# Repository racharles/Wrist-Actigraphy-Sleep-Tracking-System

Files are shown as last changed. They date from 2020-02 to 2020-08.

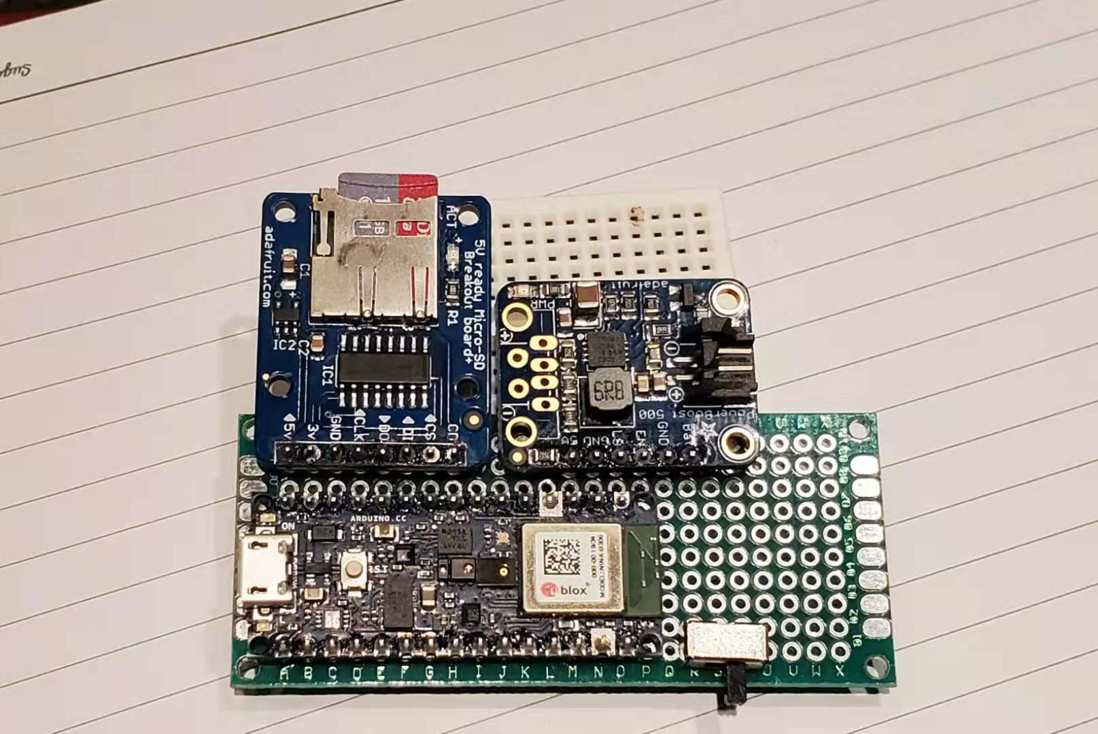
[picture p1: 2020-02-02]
Release/Hardware/WASTS V1.0 Electrical/Top View.jpg

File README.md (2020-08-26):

# Wrist Actigraphy Sleep Tracking System
Repo for the WASTS project, which entered into the 2020 LA science fair.
## Recognition
Engineering Applications Sr Division - Honorable Mention\
Darrell Smedley Award Sr Division
## References
### Academic Sources
[Stages of Sleep](https://www.sleep.org/articles/what-happens-during-sleep/)

[Interpreting PSG Reports](https://www.aastweb.org/hubfs/International%20Congress%20Presentations/4%20Atkinson%20Polysomnography%20Reports.pdf)

[Accuraccy of Wrist Actigraphy + Heart rate sensor compared to PSG](https://www.aastweb.org/hubfs/International%20Congress%20Presentations/4%20Atkinson%20Polysomnography%20Reports.pdf)

[Blood Pressure vs Sleep Quality](https://academic.oup.com/sleep/article-pdf/27/6/1097/13662447/sleep-27-6-1097.pdf)

[Comparison of Actigraphy and PSG in Older Women](https://www.ncbi.nlm.nih.gov/pmc/articles/PMC2225568/)

[Philips Actigraphy reference guide](http://www.actigraphy.com/assets/Actigraphy-reference-guide-b6bc768325426704b558b9c7288bcc07c7f636f78bec85dbafdc0814b2c62ec1.pdf)
### Datasheets
[Arduino Nano 33 BLE Sense Schematic](https://content.arduino.cc/assets/NANO33BLE_V2.0_sch.pdf)

[NINA-B3 series datasheet](https://www.u-blox.com/sites/default/files/NINA-B3_DataSheet_%28UBX-17052099%29.pdf)

[nRF52840 datasheet](https://infocenter.nordicsemi.com/pdf/nRF52840_PS_v1.1.pdf)

[LSM9DS1 datasheet](https://content.arduino.cc/assets/Nano_BLE_Sense_lsm9ds1.pdf)

[HTS221 datasheet](https://content.arduino.cc/assets/Nano_BLE_Sense_HTS221.pdf)

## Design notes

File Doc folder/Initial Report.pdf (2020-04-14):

# Low Cost Sleep Tracking with Arduino

## Rachel Bai

Purpose

The purpose of this project was to create a system that tracks the quality of sleep to decide on an appropriate wake-up time and act as advance notice for various sleep disorders.

Question

Can the quality of sleep and various sleep disorders be tracked using wrist actigraphy?

Background Research

The standard model of sleep,

Hypothesis

Main Hypothesis: Tracking the quality and health of sleep, as well as determining the optimal time for awakening, can be accomplished using wrist actigraphy.

Sub-Hypothesis: Using wrist actigraphy, movement during sleep can be detected and tracked.

Block Diagram | Schematic Diagram

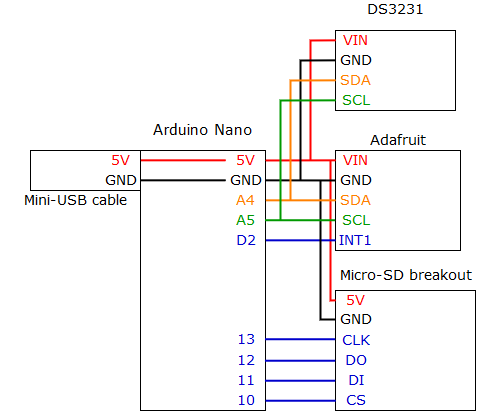
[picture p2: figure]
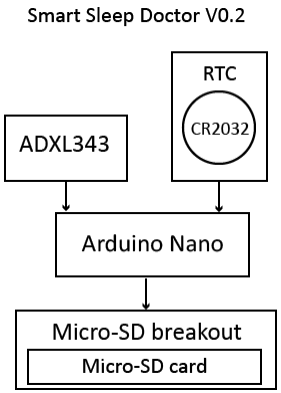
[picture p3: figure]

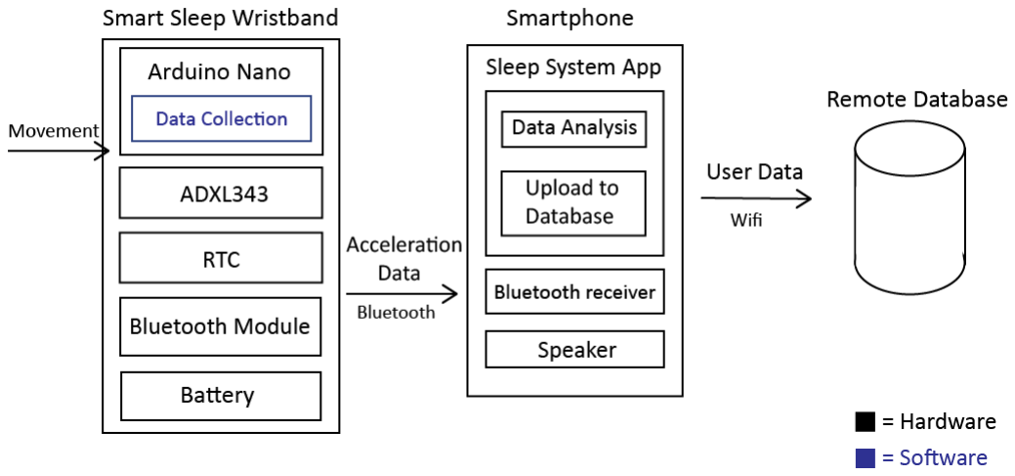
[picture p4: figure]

BOM

Name | Mass | Size | Product number | Price | Power Consumption
Arduino Nano | 7g | 18 x 45 mm | A000005 | $22 | 19 mA
Triple Axis Accelerometer breakout | 1.7g | 25.5 x 17.8 x 2.9 mm | ADXL343 | $14.95
Micro SD Storage Board | 9.1g | 25.4 x 20.32 x 2.54 mm | ADA254 | $11.89 | link (https://www.amazon.com/gp/product/B00NAY2NAI/ref=ppx_yo_dt_b_asin_title_o01_s00?ie=UTF8&psc=1)
Micro SD card | 9.1g | 1 x 15 x 10.9 mm | SDSQUAR-016G-GN6MA | $5.45 | link (https://www.amazon.com/Sandisk-Ultra-Micro-UHS-I-Adapter/dp/B073K14CVB)
Jumper Wires | 136g | 99 x 17.8 x 99 mm | B07GD2BWPY | $5.79 | link (https://www.amazon.com/EDGELEC-Breadboard-Optional-Assorted-Multicolored/dp/B07GD2BWPY?s=gateway)
RTC module | 4.5g | 43 x 22 x 15 mm | B01IXXACD0 | $6.50 | link (https://www.amazon.com/Diymore-DS3231-AT24C32-Precision-Arduino/dp/B01IXXACD0?s=gateway)
Coin cell battery | 6.8g | 30 mm diameter x 3.2 mm | B0002RID4G | $4.74 | link (https://www.amazon.com/Energizer-2032-BP-6-6-pack/dp/B0002RID4G?s=gateway)

Total Cost: $71.32

Accelerometer Comparison

We picked the ADXL343 for its range of sensitivity, low power consumption, and the built-in libraries and documentation that came with it. We also tested the MMA8451, but found that the ADXL343 had more useful features with a lower price tag.

Features | ADXL343 | ADXL335 | MMA8451
URL | https://www.adafruit.com/pr | https://www.adafruit.com/p | https://www.adafruit.com/pr
| oduct/4097 (https://www.adafruit.com/product/4097) | roduct/163 (https://www.adafruit.com/product/163) | oduct/2019 (https://www.adafruit.com/product/2019)
Dimensions | 25.5mm x 17.8mm x 2.9mm | 19mm x 19mm x 3.14mm | 21mm x 18mm x 2mm
Sensitivity range | 2-16g | 3g | 2-8g
Digital/Anal og | digital | analog | digital
# of pins | 9 | 7 | 8

Voltage | 2.0-3.6 V | 5V | 3V or 5V
Current | 23 μA | 350 μA | 6 μA to 165 μA
Weight | 1.7g | 1.27g | 1.3g
Size of IC | 3 mm × 5 mm × 1 mm | 4 mm × 4 mm × 1.45 mm | 3 mm by 3 mm by 1 mm
Additional soldering | headers | headers | headers
Interface | I2C or SPI | Analog | I2C
Integration Effort | Arduino with library | calibration and analog conversion | Arduino with library
Additional Software | library | | library
Tutorial/Exa mple | yes | calibration | yes
Interrupt pins | 2 | 2 | 2
Cost | $5.95 | $14.95 | $7.95

Software flowchart

Software design and implementation

### Final Implementation

We decided to use the Arduino Nano with the Arduino IDE for low-cost and fast prototyping. The Adafruit ADXL343 breakout board we used also came with a built-in activity interrupt, so that we were able to decrease the power consumption of the final build.

We connected the Arduino Nano, SD module, RTC, and ADXL343 based on the Schematic Diagram using a breadboard and jumper wires.

We collected data from the ADXL343 in the form of activity interrupts and printed them to the micro-SD card, along with a timestamp for each.

//print the acceleration data from the moment activity detected

data.print(event.acceleration.x); data.print(" ");

data.print(event.acceleration.y); data.print(" ");

data.println(event.acceleration.z);

//print the number of times activity detected

Serial.println("Activity detected!");

Serial.print("\tActivity Count: "); Serial.println(g_int_stats.activity, DEC);

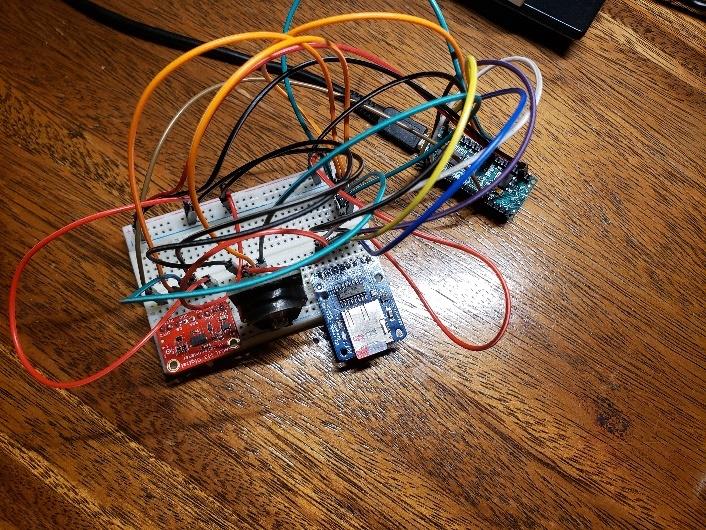
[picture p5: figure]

- Research on the standard model of sleep
- Research report placed on website
- Finished BOM and parts collected
- Acceleration on each axis printed out and stored on SD card
- RTC module added for timestamps
- Activity interrupt on ADXL343 used to notify Arduino Nano

I first did research on the standard model of sleep and collected sources about sleep and the different stages of sleep. To organize this information, I wrote a research report and put it in my website. After deciding on a schedule and two accelerometers, I added all the parts needed into the BOM and bought them online. After soldering the headers and testing the accelerometers and SD module individually, I put them together and combined the code so that the acceleration from each axis was printed in the serial monitor and micro-sd card with a timestamp. For a more efficient way to track activity, I decided to use the activity interrupt on the ADXL343 to notify the Arduino Nano. At first, the interrupt never triggered. After debugging with the example sketches and setting registers based on the datasheet, the interrupt started triggering. I adjusted the activity threshold and integrated the other components into the final sketch.

### Testing

We first tested the ADXL343 alone by outputting the data to the serial monitor and checking if it was calibrated properly.

### Evaluation

Gantt Chart

Timeline | 6/4 | 6/8 | 6/11 | 6/15 | 6/16 | 6/18 | 6/22 | 6/25 | 6/29 | 7/2
Milestones | | | Website v1.0 | | Block Diagram v1.0 | | Code for prototype | Prototype v0.1 | | Prototype v0.2
| | | Research Paper v0.5 | | Schematic v1.0 | | All parts bought
| | | | | BOM v1.0
1. Learn:
Research sleep literature

Research existing technologies

Develop project website
2. Design:
Use case

Block Diagram

BOM (parts list)

Circuit Schematic
3. Build:
Buy parts

Prototype with accelerometer

Prototype with SD and RTC
4. Test:
Test for activity sensing

Evaluate
5. Document:
website

Research report

Project Report

Results

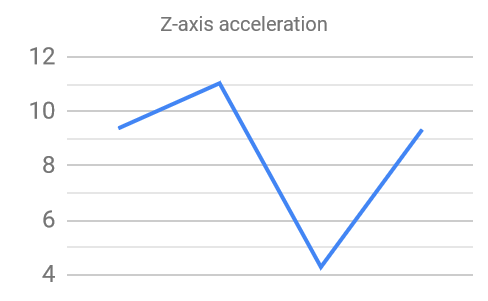
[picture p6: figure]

Upward and downward motion on z-axis

X- axis | Y-axis | Z-axis
-0.24 | 0.51 | 9.38
-1.45 | 0.2 | 11.04
-0.43 | -2.31 | 4.28 | Activity detected
-0.2 | 0.24 | 9.34

Rotation from z-axis to x-axis

X-axis | Y-axis | Z-axis
-0.24 | 0.12 | 9.38
0.9 | -0.16 | 10.63
5.96 | 0 | 6.47 Activity detected
9.07 | 0.27 | 2.71
9.85 | -0.08 | 0.9

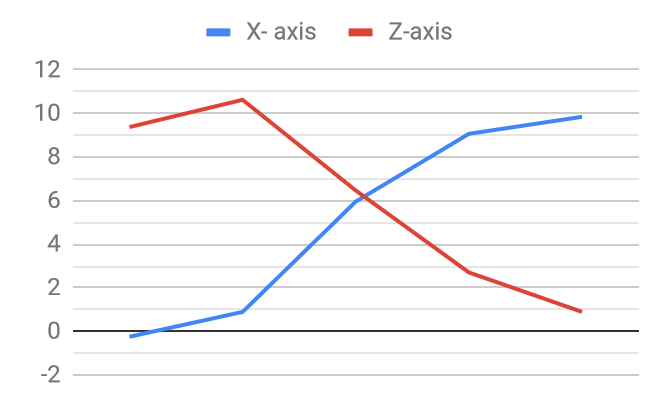
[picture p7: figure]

Lines of Code | 130
Frameworks | 1.8.9
Libraries | Wire, RTClib, SD, Adafruit_Sensor, Adafruit_ADXL343
Calibration | ADXL343 activity threshold set to 20

The activity tracking feature on the ADXL343 detects activity when the change in acceleration on any axis surpasses a certain threshold. Using a threshold is most effective in measuring larger movement, and smaller movements are often missed by the sensor. However, movements during sleep are usually small. This problem was fixed by changing the sensitivity. Because the sensor is mounted on the wrist, the two main types of movement are linear motion and rotation. The ADXL343 is able to accurately detect these types of movement. Using this system, movement during sleep can be tracked accurately.

I learned how to solder through-hole pins and the process of checking each pin to make sure the connection is reliable and there is no connection between VIN and GND, which would cause a short circuit.

We had trouble using the activity interrupt on the ADXL343, where it seemed like the Arduino was not accepting any input. When checking if the interrupt was firing by measuring the voltage of the interrupt line, there was a voltage difference, which meant the interrupt was firing, but the Arduino was not detecting it. I decided to look at the ADXL343 library and datasheet, and I saw that the library set up the single tap registers in the begin function, so we set the activity inactivity control register to 1. However, this also didn’t work. The registers had to be set in binary, so a setting of 1 did not turn everything on, it turned the last setting on. After changing the number, the activity interrupt finally started working.

In the future, we plan on integrating this part of the project into the final design by compressing the build, testing during full nights of sleep, and advancing the movement detection algorithm.

Bibliography

Full Code

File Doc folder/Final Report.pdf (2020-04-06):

# Low Cost Sleep Quality Tracking Using Arduino

## Rachel Bai

## The Webb Schools

## Abstract:

Sleep trackers that use actigraphy are a lower cost alternative to traditional overnight PSG (Polysomnography) sleep labs, and offer more mobility and access to people who might not have access to a sleep lab. However, many commercial sleep trackers can still cost more than one hundred dollars. Using Arduino in conjunction with a 3D printed case and easily accessible materials, we were able to make a cheap wrist-mounted sleep tracker that can accurately track several AASM standards of sleep, including sleep efficiency, sleep onset latency, and WASO events. After the data was collected, it was processed using Python and then R studio. A positive correlation was found between the self-reported sleeping quality measures and the device collected standards, indicating the feasibility of much lower-cost sleep trackers with Arduino. The next phase of this project would focus Bluetooth connectivity, automated data processing, and cloud-based data storage.

Introduction:

Sleep is a massively overlooked aspect of general health and cognitive function. In a poll by the National Sleep Foundation, the daily effectivity of U.S. Adults increased directly with the perceived quality of sleep[4]. For many, poor sleep quality can also be an indicator of sleeping disorders or other underlying health issues. The standard for measuring objective sleep quality is the American Academy of Sleep Medication (AASM) recommended reporting parameters, which uses total recording time (TRT), total sleep time (TST), sleep efficiency, sleep onset latency, and wake after sleep onset (WASO) events[1]. In order to measure these parameters, researchers typically use a polysomnography machine (PSG), which can often be expensive, bulky, and intrusive. The development of fitness trackers such as the Fitbit and other smart watches that use actigraphy to track sleep has introduced a lower cost option for long-term sleep quality tracking[3]. Purely actigraphy-based sleep trackers are about 60% effective in finding the different stages of sleep compared to overnight sleep studies, but are frequently more than 80% effective in determining the start and end times of periods of sleep [5].

Research Question:

Is it possible to create a wrist-mounted sleep tracker that provides a low-cost and accessible platform for long-term sleep quality tracking?

Hypothesis:

Using a low-cost data collection system built using Arduino that collects actigraphy data, several AASM sleep quality standards, including sleep efficiency, sleep onset latency, and WASO events can be tracked.

## Methodology:

Materials:

Name | Seller | Description | Price | URL
Arduino 33 BLE Sense | Arduino | small mcu with built-in sensors and BLE | $31.50 | link (https://store.arduino.cc/usa/nano-33-ble-sense-with-headers)
Micro SD Storage Board | Amazon | micro sd module for arduino | $11.89 | link (https://www.amazon.com/gp/product/B00NAY2NAI/ref=ppx_yo_dt_b_asin_title_o01_s00?ie=UTF8&psc=1)
Micro SD card | Amazon | 8 gb micro sd card | $5.45 | link (https://www.amazon.com/dp/B001CQT0X4/ref=dp_cerb_1)
Micro Lipo w/MicroUSB Jack v1 | Adafruit | micro lipo charger | $10.16 | link (https://www.amazon.com/gp/product/B00MJ0HOKS/ref=ppx_yo_dt_b_asin_title_o03_s01?ie=UTF8&psc=1)
Adafruit PowerBoost 500 | Adafruit | 3.7v to 5v booster | $11.52 | link (https://www.amazon.com/Adafruit-PowerBoost-500-Basic-ADA1903/dp/B00OKJFKEI?s=electronics)
Lithium Ion Polymer Battery - 3.7v 1000mAh | Amazon | lipo battery | $9.99 | link (https://www.amazon.com/1000mAh-battery-Rechargeable-Lithium-Connector/dp/B07BTW7CJY)
Nylon watch straps | Amazon | nylon black watch straps with buckles | $11.99 | link (https://www.amazon.com/BARTON-Watch-Bands-Choice-Standard/dp/B015NKHV2G)
Medical felt padding | Amazon | 1/8 inch felt adhesive for medical use | $18.45 | link (https://www.amazon.com/gp/product/B0053D30TC/ref=ppx_yo_dt_b_asin_title_o05_s00?ie=UTF8&psc=1)
3-pin switch | Polulu | 3 pin mini slide switch | $1.50 | link (https://www.pololu.com/product/1408)
Stranded wire kit | Amazon | 22 awg stranded core wire | $18.99 | link (https://www.amazon.com/gp/product/B00B4ZQ3L0/ref=ppx_yo_dt_b_asin_title_o00_s00?ie=UTF8&psc=1)
Tacklife Digital Multimeter | Amazon | digital multimeter | $26.97 | link (https://www.amazon.com/Tacklife-DM01M-Multimeter-Detection-Temperature/dp/B01M7ZD1VN)
Soldering Station | Amazon | Weller 40 watt soldering station | $38.97 | link (https://www.amazon.com/Weller-WLC100-40-Watt-Soldering-Station/dp/B000AS28UC)
Solder Wire | Amazon | 60/40 solder wire, 0.8mm | $7.99 | link (https://www.amazon.com/MAIYUM-63-37-Solder-Electrical-Soldering/dp/B075WB98FJ?s=hi)
3/8 inch screws | Ace Hardware | 3/8 inch pan head screws | $0.30 | link (https://www.acehardware.com/departments/hardware/screws-and-anchors/sheet-metal-screws/56192)

Hardware:

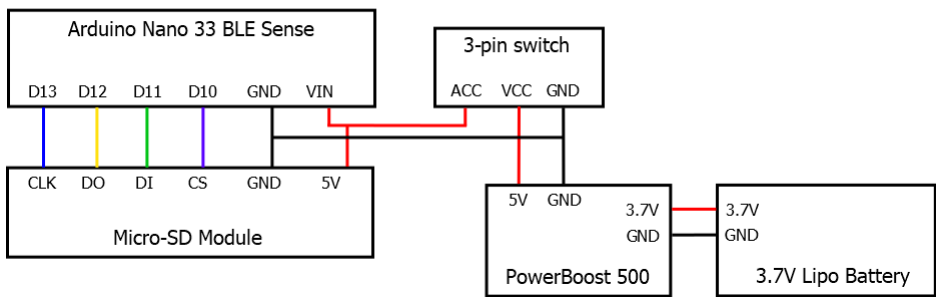
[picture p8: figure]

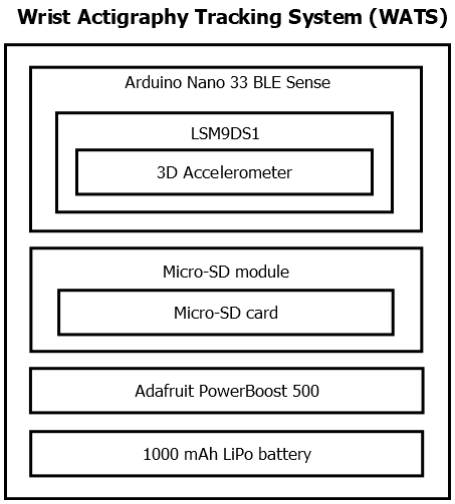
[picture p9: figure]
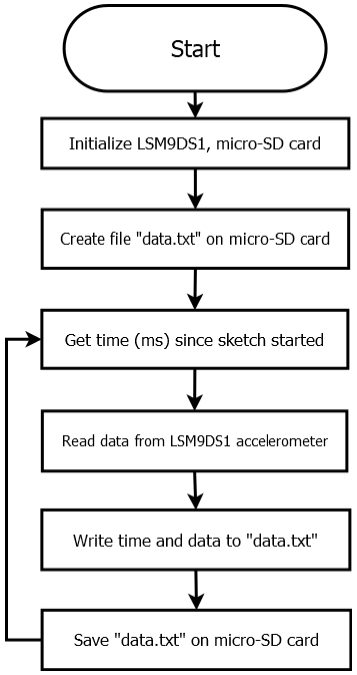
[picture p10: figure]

Software:

Software: Arduino IDE, Python, R Studio, Github

Tools: VSCode, Autodesk Inventor, Soldering Iron, 3D printer

Planning:

Arduino was chosen as the platform for the Wrist Actigraphy Tracking System (WATS) for the ease in programming and prototyping, as well as the built-in sensors and low power consumption of the Arduino Nano 33 BLE Sense board. The built-in 9-axis IMU of the Arduino BLE Sense was used as an accelerometer to measure movement. A micro-SD module, connected to the Arduino using SPI was used as external storage for the recorded data. Because of the size and weight constraints, a lightweight LiPo battery was chosen as a power source. However, commercially available LiPo batteries have a nominal voltage of 3.7 volts, so the Adafruit PowerBoost 500 was used to maintain 5.2 volts to power the Arduino board. After measuring the power consumption of the device to be 55.6 mA, a 1000 mAh LiPo battery was chosen to provide ~20 hours of continuous power.

Building Process:

Before soldering, the electrical components were connected on a breadboard using jumper cables. Once the layout was finalized, each component was soldered onto a protoboard and connections were made by soldering 22 gauge wires to each soldered pin. The Arduino Nano 33 BLE Sense, Adafruit micro-SD module, Adafruit PowerBoost 500 module, and a 3-pin switch were soldered onto protoboards. To conserve power and prevent distracting lights during overnight sleep trials, each non-essential LED was de-soldered from the boards. To design the 3D case, the finished electrical components were measured to get the necessary dimensions for the box. A lid was designed to be held to the box body using screws. After the first prototypes of the 3D box had some small issues, the overhangs were changed and the box was made slimmer. A nylon watch strap and plastic buckle was then attached to each device’s case.

Programming:

Using C++ with the Arduino environment, a program was written that used the built in
LSM9DS1 and SD card module libraries to read from the built-in IMU on the Arduino board and wrote the data to an inserted micro-SD card. A zero-delay timer was used instead of the built-in delay() function in order to maintain a faster sampling rate. Based on research into sampling rates and movement speeds, a sampling rate of 5 Hz was chosen.

## Results

After the accelerometer data was collected from the micro-SD card, the raw data x(t), y(t), and z(t) was composed into the magnitude Act(t) [5] using Python and written into an Excel file.

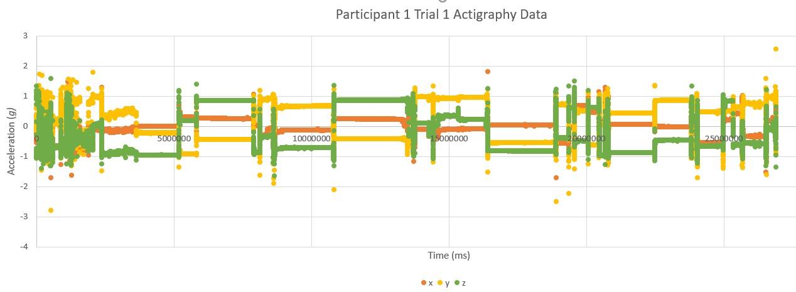
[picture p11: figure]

act(t) = √x(t)
2 + y(t)

2 + z(t)

2

In order to validate that the actigraphy data collected by the sleep tracking device could be used to identify AASM standards of sleep quality, the actigraphy data was processed using Python to convert the raw data into the mean, median, maximum, and 95th percentile of each 3-min epoch.

Using R-Studio, each epoch was classified as either wake or sleep, which allowed the

To classify each epoch as active or inactive, we used the mean of each epoch to decide if it was an outlier or not. The formula we used was mean < (25th percentile – 1.5 * IQR) or mean > (75th percentile +1.5 * IQR).

In order to find the total sleep time, we counted the total number of inactive epochs in the trial.

To find the sleep efficiency, we divided the total time spent asleep by the total number of recorded epochs.

To find the sleep latency, we found the first four epochs, which is 12 minutes, with continued inactivity, and defined the start of sleep as the start of those four epochs [6]. Sleep latency was calculated by finding the number of epochs up to the start of sleep epoch.

Using the questions from the questionnaire, the measured standards were compared to the self-reported questions.

Correlation Metrics:

Measure | Correlation | P-Value
Sleep Latency | -0.397 | 0.2
Total Sleep Time | 0.863 | 7e-05

## Discussion:

Based on our results, the device is able to accurately track movement and periods of inactivity and activity during sleep when compared to the self-reported metrics of sleep quality. However, it is not very accurate at matching the participant’s self reported sleep onset latency measures.

## Conclusion:

This low cost sleep tracker can be used to track sleep, offering a lower cost alternative to commercial sleep trackers like the Fitbit. Based on our results, the device is able to track movement and periods of inactivity and activity during sleep when compared to the self-reported metrics of sleep quality, as well as track total sleep time and WASO events.

Currently the data has to be processed manually by taking out the micro-SD card from the device and using Python and R, but the process can be streamlined by using the built-in Bluetooth capabilities of the Arduino Nano 33 BLE Sense. In the future, we plan on improving the accuracy of the sleep tracking by adding secondary sensory data, such as an EEG to track heart rate or a humidity/temperature sensor. The electronic components were the limiting factor in size and cost, so a custom-made PCB board would be not only cheaper to mass-produce, but also allows for a smaller form factor for the comfort of the wearer. The analysis of the data can also be improved by applying machine learning to personalize the quality analysis.

## References:

1. Atkinson, J. (n.d.). Polysomnography Reports –Interpreting the Data. Retrieved from https://www.aastweb.org/hubfs/International Congress Presentations/4 Atkinson Polysomnography Reports.pdf
2. Blackwell, T., Redline, S., Ancoli-Israel, S., Schneider, J. L., Surovec, S., Johnson, N. L., … Study of Osteoporotic Fractures Research Group (2008). Comparison of sleep parameters from actigraphy and polysomnography in older women: the SOF study. Sleep, 31(2), 283–291. doi:10.1093/sleep/31.2.283
3. Martin, J. L., & Hakim, A. D. (2011). Wrist actigraphy. Chest, 139(6), 1514–1527. doi:10.1378/chest.10-1872
4. National Sleep Foundation's 2018 Sleep in America® Poll Shows Americans Failing to Prioritize Sleep. (n.d.). Retrieved from https://www.sleepfoundation.org/press-release/national-sleep-foundations-2018-sleep-americar-poll-shows-americans-failing
5. Yuda, Emi, et al. “Sleep Stage Classification by a Combination of Actigraphic and Heart Rate Signals.” Journal of Low Power Electronics and Applications, vol. 7, no. 4, 2017, p. 28., doi:10.3390/jlpea7040028.
6. Maglione, Jeanne E et al. “Actigraphy for the assessment of sleep measures in Parkinson's disease.” Sleep vol. 36,8 1209-17. 1 Aug. 2013, doi:10.5665/sleep.2888

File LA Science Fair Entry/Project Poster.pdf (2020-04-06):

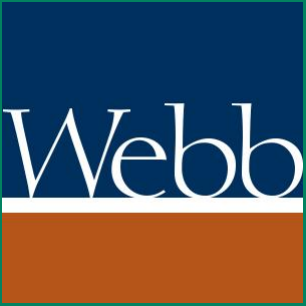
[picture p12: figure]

# Low Cost Sleep Quality Tracking Using Arduino

# Rachel Bai, The Webb Schools

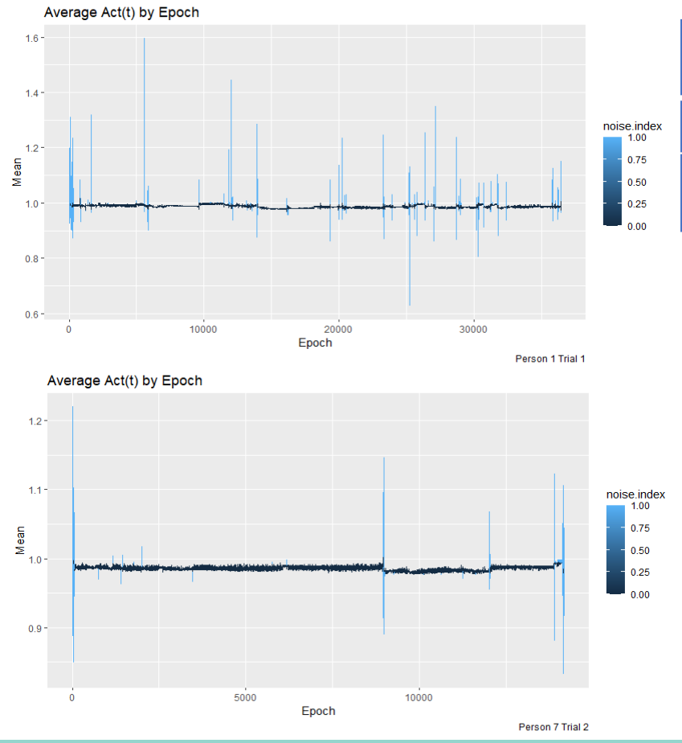
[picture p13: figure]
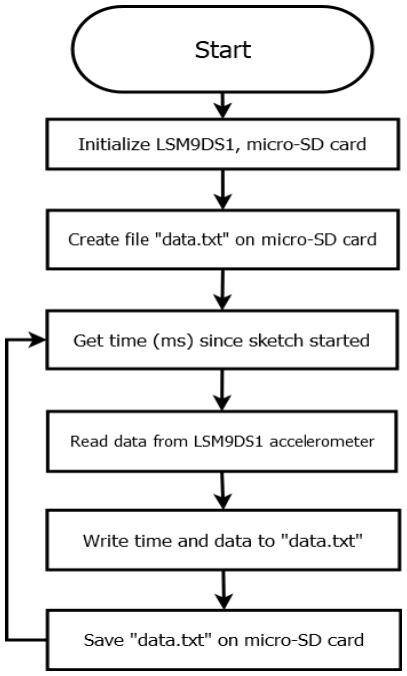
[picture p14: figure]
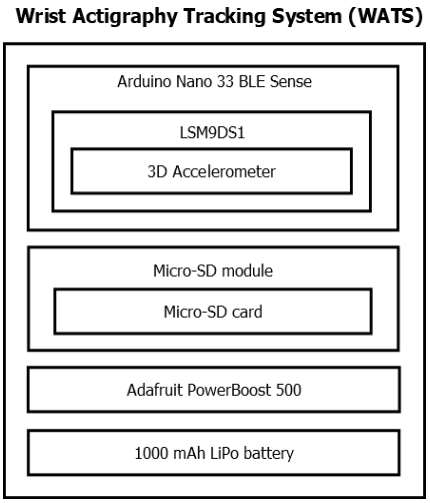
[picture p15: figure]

1. Atkinson, J. (n.d.). Polysomnography Reports –Interpreting the Data. Retrieved from https://www.aastweb.org/hubfs/International Congress Presentations/4 Atkinson Polysomnography Reports.pdf
2. Blackwell, T., Redline, S., Ancoli-Israel, S., Schneider, J. L., Surovec, S., Johnson, N. L., … Study of Osteoporotic Fractures Research Group (2008). Comparison of sleep parameters from actigraphy and polysomnography in older women: the SOF study. Sleep, 31(2), 283–291. doi:10.1093/sleep/31.2.283
3. Martin, J. L., & Hakim, A. D. (2011). Wrist actigraphy. Chest, 139(6), 1514–1527. doi:10.1378/chest.10-1872
4. National Sleep Foundation's 2018 Sleep in America® Poll Shows Americans Failing to Prioritize Sleep. (n.d.). Retrieved from https://www.sleepfoundation.org/press-release/national-sleepfoundations-2018-sleep-americar-poll-shows-americans-failing
5. Yuda, Emi, et al. “Sleep Stage Classification by a Combination of Actigraphic and Heart Rate Signals.” Journal of Low Power Electronics and Applications, vol. 7, no. 4, 2017, p. 28., doi:10.3390/jlpea7040028.

# Abstract

# Introduction

# Methodology

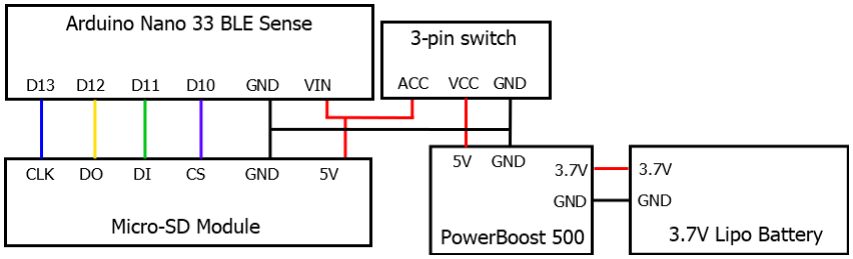
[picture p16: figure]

# Results

# Conclusion

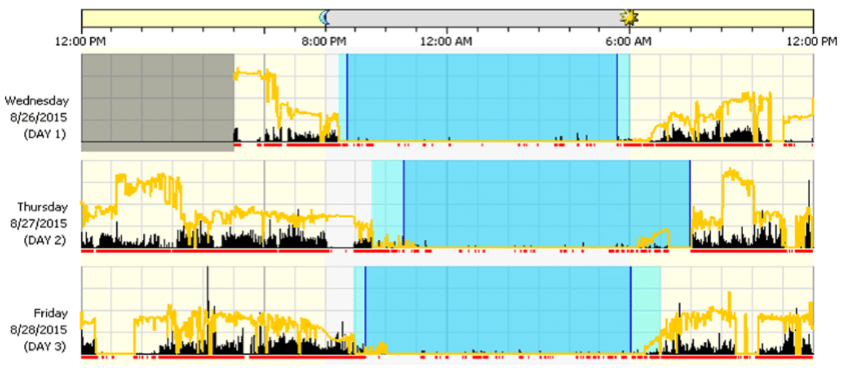
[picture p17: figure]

# Acknowledgements

Sleep trackers that use actigraphy are a lower cost alternative to traditional overnight PSG (Polysomnography) sleep labs, and offer more mobility and access to people who might not have access to a sleep lab. However, many commercial sleep trackers can still cost more than one hundred dollars. Using Arduino in conjunction with a 3D printed case and easily accessible materials, we were able to make a cheap wrist-mounted sleep tracker that can accurately track several AASM standards of sleep, including sleep efficiency, sleep onset latency, and WASO events. After the data was collected, it was processed using Python and then R studio. A positive correlation was found between the self-reported sleeping quality measures and the device collected standards, indicating the feasibility of much lowercost sleep trackers with Arduino. The next phase of this project would focus Bluetooth connectivity, automated data processing using machine learning, and improved comfort for the user of the device.

Sleep is a massively overlooked aspect of general health and cognitive function. In a poll by the National Sleep Foundation, the daily effectivity of U.S. Adults increased directly with the perceived quality of sleep[4]. For many, poor sleep quality can also be an indicator of sleeping disorders or other underlying health issues. The standard for measuring objective sleep quality is the American Academy of Sleep Medication (AASM) recommended reporting parameters, which uses total recording time (TRT), total sleep time (TST), sleep efficiency, sleep onset latency, and wake after sleep onset (WASO) events[1]. In order to measure these parameters, researchers typically use a polysomnography machine (PSG), which can often be expensive, bulky, and intrusive. The development of fitness trackers such as the Fitbit and other smart watches that use actigraphy to track sleep has introduced a lower cost option for long-term sleep quality tracking [3]. Purely actigraphy-based sleep trackers are frequently more than 80% effective in determining the start and end times of periods of sleep [5].

Electrical Components
Arduino Nano 33 BLE Sense
Micro-SD module
Micro-SD card
Adafruit PowerBoost 500
3.7v 1000 mAh Lipo battery Mini slide switch
22 AWG stranded wire

Software
Arduino, Python, R Studio, GitHub

Tools
Soldering Iron
3D printer
Visual Studio Code
Autodesk Inventor

Arduino was chosen as the platform for the Wrist Actigraphy Tracking System (WATS) for the ease in programming and prototyping, as well as the built-in sensors and low power consumption of the Arduino Nano 33 BLE Sense board. The built-in 9-axis IMU of the Arduino BLE Sense was used as an accelerometer to measure movement. A micro-SD module, connected to the Arduino using SPI was used as external storage for the recorded data. Because of the size and weight constraints, a lightweight LiPo battery was chosen as a power source. However, commercially available LiPo batteries have a nominal voltage of 3.7 volts, so the Adafruit PowerBoost 500 was used to maintain 5.2 volts to power the Arduino board. After measuring the power consumption of the device to be 55.6 mA, a 1000 mAh LiPo battery was chosen to provide ~20 hours of continuous power. A schematic was drawn with all connections between components. When the electrical connections were finalized, the components were arranged and soldered onto a double sided perf board, and connections were made with 22 AWG stranded wire according to the schematic. A 3D printable case was designed for the device using Inventor with cutouts for the micro-SD card, switch, and micro-USB port on the Arduino.
Self selected participants(n=7) wore the WATS device on their wrist during overnight trials. Each participant also filled out a sleep quality questionnaire with questions asking about sleep onset latency, total sleep time, and WASO events after they woke up. The data was collected from the WATS device and processed further.

This low cost sleep tracker can be used to track sleep, offering a lower cost alternative to commercial sleep trackers like the Fitbit. Based on our results, the device is able to track movement and periods of inactivity and activity during sleep when compared to the self-reported metrics of sleep quality, as well as track total sleep time and WASO events.

Hardware Components
Nylon watch straps with buckles Medical felt padding
MakerBot PLA
3/8 inch screws

# Objective

The LSM9DS1 accelerometer which was used to measure movement during sleep had an accuracy of ±90 mg on the ±4g default setting. It was able to capture noticeable movements on all three axes during the calibration procedure and overnight trials.

After the accelerometer data was collected from the micro-SD card, the raw data x(t), y(t), and z(t) was composed into the magnitude Act(t) [5] using Python.

## act t = x t

2 + y t

2 + z t

2

The Python script separated the data into 3-min epochs with the mean, median, max, and 95

th percentile of each epoch. The average activity of each epoch was used to split epochs into the active or inactive categories. Using this classification, sleep latency, total sleep time, and sleep efficiency could be calculated.

## The objective of this project was to create a low cost, wrist-mounted data collection device using Arduino that collects

actigraphy data in order to track overnight sleep quality.

# Final Device

Currently the data has to be processed manually by taking out the micro-SD card from the device and using Python and R, but the process can be streamlined by using the built-in Bluetooth capabilities of the Arduino Nano 33 BLE Sense. In the future, we plan on improving the accuracy of the sleep tracking by adding secondary sensory data, such as an EEG to track heart rate or a humidity/temperature sensor. The electronic components were the limiting factor in size and cost, so a custom-made PCB board would be not only cheaper to mass-produce, but also allows for a smaller form factor for the comfort of the wearer. The analysis of the data can also be improved by applying machine learning to personalize the quality analysis.

# Future Direction

Measure | Correlation | P-Value
Sleep Latency | -0.397 | 0.2
Total Sleep Time | 0.863 | 7e-05

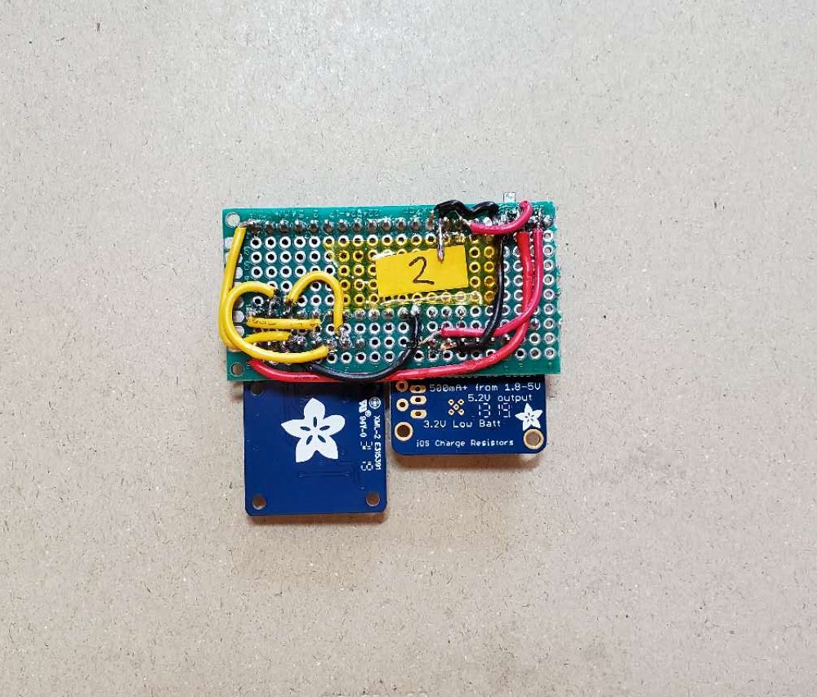
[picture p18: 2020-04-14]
Hardware/Electronics/WASTS V1.0/Bottom View.jpg

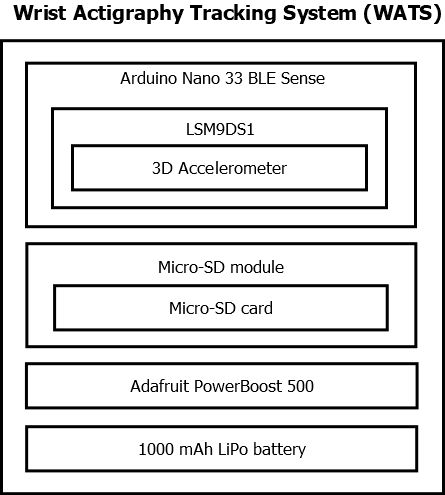
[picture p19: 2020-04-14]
Hardware/Electronics/WASTS V1.0/Block Diagram.png

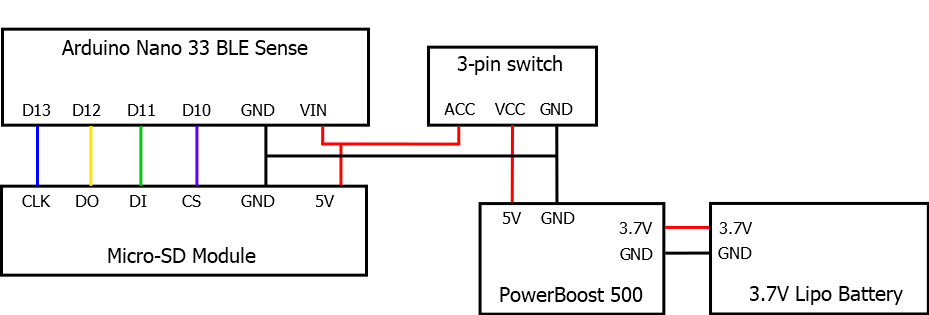
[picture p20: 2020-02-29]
Hardware/Electronics/WASTS V1.0/Schematic.png

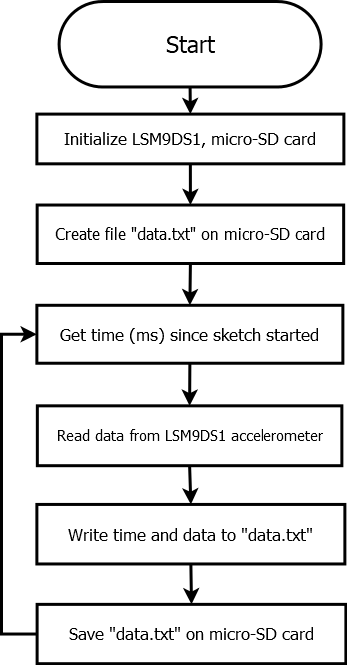
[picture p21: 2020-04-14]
Doc folder/Diagrams/WASTS V1.0 Software Flow Chart.png

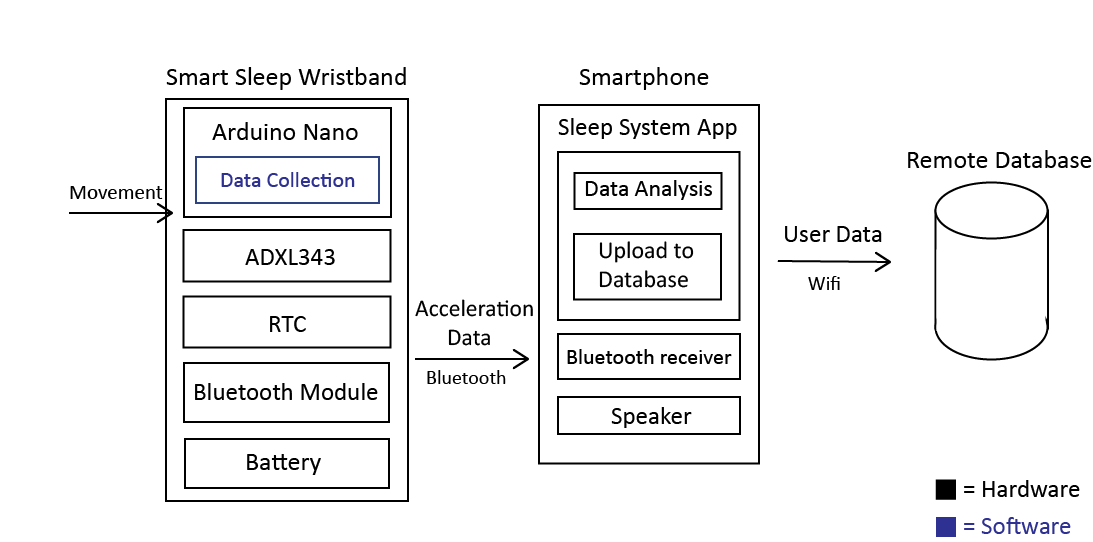
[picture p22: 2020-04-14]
Doc folder/Diagrams/Future Work Context Diagram.png

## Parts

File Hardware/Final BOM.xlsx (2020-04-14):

 | Name | Seller | Description | Product number | Price | URL
Sleep System V1.0 | Arduino 33 BLE Sense | Arduino | small mcu with built-in sensors and BLE | 7630049201576 | $31.50 | link (https://store.arduino.cc/usa/nano-33-ble-sense-with-headers)
 | Micro SD Storage Board | Amazon | micro sd module for arduino | ADA254 | $11.89 | link (https://www.amazon.com/gp/product/B00NAY2NAI/ref=ppx_yo_dt_b_asin_title_o01_s00?ie=UTF8&psc=1)
 | Micro SD card | Amazon | 8 gb micro sd card | B001CQT0X4 | $5.45 | link (https://www.amazon.com/dp/B001CQT0X4/ref=dp_cerb_1)
 | Micro Lipo w/MicroUSB Jack v1 | Adafruit | micro lipo charger | ADA1904 | $10.16 | link (https://www.amazon.com/gp/product/B00MJ0HOKS/ref=ppx_yo_dt_b_asin_title_o03_s01?ie=UTF8&psc=1)
 | Adafruit PowerBoost 500 | Adafruit | 3.7v to 5v booster | ADA1903 | $11.52 | link (https://www.amazon.com/Adafruit-PowerBoost-500-Basic-ADA1903/dp/B00OKJFKEI?s=electronics)
 | Lithium Ion Polymer Battery - 3.7v 1000mAh | Amazon | lipo battery | YDL2018032923 | $9.99 | link (https://www.amazon.com/1000mAh-battery-Rechargeable-Lithium-Connector/dp/B07BTW7CJY)
 | Nylon watch straps | Amazon | nylon black watch straps with buckles | B07J4PQ79M | $11.99 | link (https://www.amazon.com/BARTON-Watch-Bands-Choice-Standard/dp/B015NKHV2G)
 | Medical felt padding | Amazon | 1/8 inch felt adhesive for medical use | COMINSO5JUL15980 | $18.45 | link (https://www.amazon.com/gp/product/B0053D30TC/ref=ppx_yo_dt_b_asin_title_o05_s00?ie=UTF8&psc=1)
 | 3-pin switch | Polulu | 3 pin mini slide switch | #1408 | $1.50 | link (https://www.pololu.com/product/1408)
 | Stranded wire kit | Amazon | 22 awg stranded core wire | 27WK22STR25 | $18.99 | link (https://www.amazon.com/gp/product/B00B4ZQ3L0/ref=ppx_yo_dt_b_asin_title_o00_s00?ie=UTF8&psc=1)
 | Tacklife Digital Multimeter | Amazon | digital multimeter | D01M | $26.97 | link (https://www.amazon.com/Tacklife-DM01M-Multimeter-Detection-Temperature/dp/B01M7ZD1VN)
 | Soldering Station | Amazon | Weller 40 watt soldering station | WLC100 | $38.97 | link (https://www.amazon.com/Weller-WLC100-40-Watt-Soldering-Station/dp/B000AS28UC)
 | Solder Wire | Amazon | 60/40 solder wire, 0.8mm | JF850 | $7.99 | link (https://www.amazon.com/MAIYUM-63-37-Solder-Electrical-Soldering/dp/B075WB98FJ?s=hi)
 | 4x 3/8 inch screws | Ace Hardware | 3/8 inch pan head screws | 56192 | $0.75 | link (https://www.acehardware.com/departments/hardware/screws-and-anchors/sheet-metal-screws/56192)

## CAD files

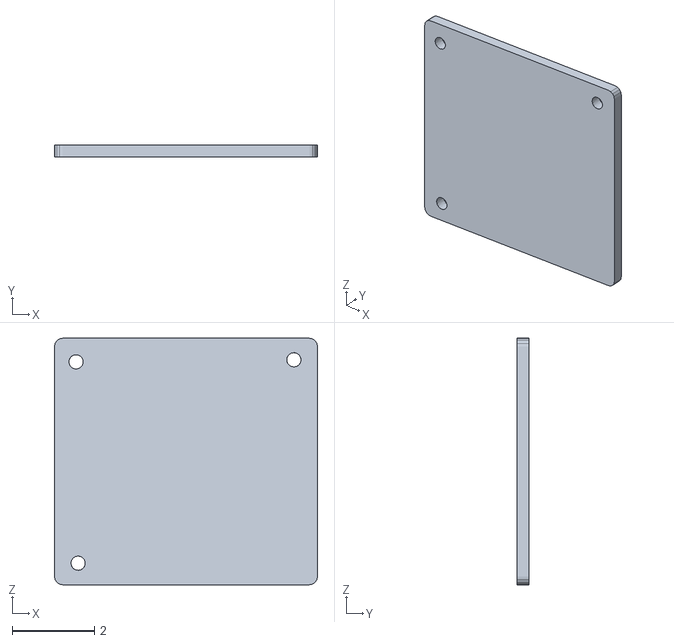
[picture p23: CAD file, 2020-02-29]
Hardware/Mechanical/WASTS V1.0 Case Design/WASTS box lid.stl
6.40 x 0.3 x 6.00

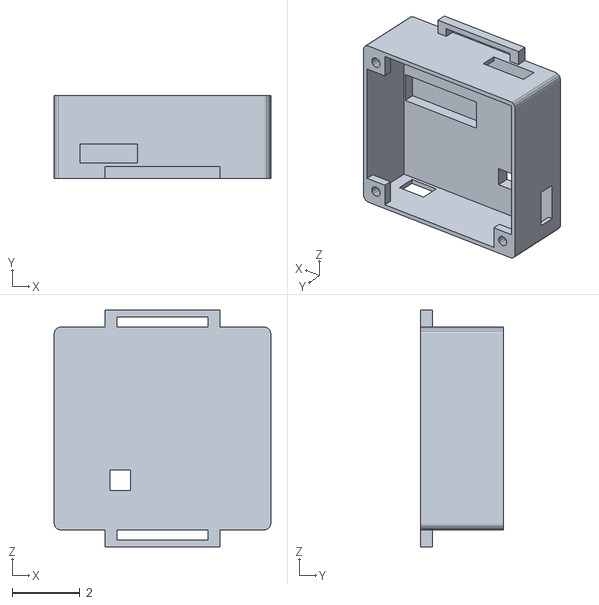
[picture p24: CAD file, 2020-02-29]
Hardware/Mechanical/WASTS V1.0 Case Design/WASTS box body.stl
6.40 x 2.45 x 7.00

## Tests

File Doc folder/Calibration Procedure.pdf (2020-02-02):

Calibration Procedure:

1. Start with the wristwatch secured on the wrist, insert a mirco-SD card into the slot, and turn the switch on.
2. Keep the wrist in a horizontal position with the watch facing up.
3. Rotate wrist 180 degrees CCW
4. Rotate wrist 180 degrees CW
5. Repeat 2 + 3 x2 with 1 second movements
6. Repeat 2 + 3 x2 with 2 second movements
1. Start with elbow bent, the arm facing upwards, and the wrist facing left
2. Rotate arm around elbow 90 CW, towards the right arm
3. Rotate arm around elbow 90 CCW, away from the right arm
4. Repeat 2 + 3 x2 with 1 second movements
5. Repeat 2 + 3 x2 with 2 second movements
1. Start with the arm and wrist in a horizontal position with the watch facing up.
2. Rotate arm around elbow 90 CW, towards the chest, maintaining a horizontal position.
3. Rotate arm around elbow 90 CCW, away from the chest
4. Repeat 2 + 3 x2 with 1 second movements
5. Repeat 2 + 3 x2 with 2 second movements
1. Start with the wrist facing to the left and the arm stretched away from the body to the left.
2. Rotate arm around shoulder horizontally 90 CW, towards the right arm.
3. Rotate arm around shoulder horizontally 90 CCW, away from the right arm
4. Repeat 2 + 3 x2 with 1 second movements
5. Repeat 2 + 3 x2 with 2 second movements

Turn the switch off, take the wristwatch off, and take the micro-SD card out of the device.

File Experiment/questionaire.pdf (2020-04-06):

Experienced Sleep Quality Questionnaire

Participant Name: ______________________

Trial #: ___

What is your age? ______

What gender do you identify as? ___________

Do you have any pre-existing sleep disorders? Y / N

Do you currently have any health conditions that may affect the quality of your sleep? Y / N

How was your experienced quality of your sleep last night, on a scale from 1=worst to 10=best?

1 | 2 | 3 | 4 | 5 | 6 | 7 | 8 | 9 | 10

How many times do you think you woke up after falling asleep last night?

______

How long (in hours or minutes) do you think it took for you to fall asleep?

______

How long (in hours or minutes) do you think you slept last night?

______

Reminder: You can opt-out of this questionnaire at any time, and if you choose to

do so, your data and personal information will not be used in this project and will

be immediately deleted.

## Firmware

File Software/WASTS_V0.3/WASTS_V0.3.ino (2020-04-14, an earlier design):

/*******************************************************************************
WASTS
Rachel Bai
v0.3
Last edited: 11/12/2019

Samples accelerometer, humidity, and temperature data from ADXL343 and BME280
sensors using activity and inactivity HW interrupts and prints the data to a
micro-SD card.

HW config:
Arduino Nano
micro-SD module
ADXL343
BME280
2000mAh 3.7v lipo battery
Adafruit PowerBoost 500
DS3231 RTC

CHANGES: Removed LCD, split data types into different files

Libraries from Arduino and Adafruit
*******************************************************************************/

#include <Wire.h>
#include <RTClib.h>
#include <SD.h>
#include <Adafruit_Sensor.h>
#include <Adafruit_ADXL343.h>
#include <Adafruit_BME280.h>

//constants
const int baud_rate = 9600;
const int print_delay = 50;

unsigned long previousMillis = 0;
const long read_interval = 2000; //read from bme280 every 2 seconds


//assign an I2C address to the ADXL343
Adafruit_ADXL343 accel = Adafruit_ADXL343(12345);

//assign an I2C address to BME280
Adafruit_BME280 bme;

RTC_DS3231 rtc; //create RTC object
File data; //create new file on SD card to store data in

//pin for activity interrupt on the Arduino
const int INPUT_PIN_INT1 = 2;
const int INPUT_PIN_INT2 = 3;

//struct stores the # of activity/inactivity interrupts fired
struct adxl_int_stats {
    uint32_t inactivity;
    uint32_t activity;
};

struct adxl_int_stats g_int_stats = { 0 }; //global stats block
uint32_t g_int1_fired = 0; //counter for number of unused interrupts
uint32_t g_int2_fired = 0; //counter for number of unused interrupts
int_config g_int_config_enabled = { 0 }; //variable for enabled interrupts
int_config g_int_config_map = { 0 }; //variable for mapping INT pin interrupts


/**
 * Name: int1_isr
 * Inputs: void
 * Returns: void
 * Interrupt service routine for INT1 pin event, triggers interrupt handler in
 * the main loop and increments counter for number of times the activity interrupt
 * is triggered
*/
void int1_isr(void) {
    g_int_stats.activity++; //counter
    g_int1_fired++; //trigger interrupt handler in loop
}

/**
 * Name: int2_isr
 * Inputs: void
 * Returns: void
 * Interrupt service routine for INT1 pin event, triggers interrupt handler in
 * the main loop and increments counter for number of times the inactivity interrupt
 * is triggered
*/
void int2_isr(void) {
    g_int_stats.inactivity++; //counter
    g_int2_fired++; //trigger interrupt handler in loop
}

/**
 * Name: config_interrupts
 * Inputs: void
 * Returns: void
 * Configuration for the ADXL343 INT1 and INT2 HW interrupts
*/
void config_interrupts(void) {
    //attach the INT1 input pin on the Arduino to the ISR for the INT1 on the ADXL343
    pinMode(INPUT_PIN_INT1, INPUT);
    attachInterrupt(digitalPinToInterrupt(INPUT_PIN_INT1), int1_isr, RISING);

    //attach the INT2 input pin on the Arduino to the ISR for the INT2 on the ADXL343
    pinMode(INPUT_PIN_INT2, INPUT);
    attachInterrupt(digitalPinToInterrupt(INPUT_PIN_INT2), int2_isr, RISING);

    //enable activity and inactivity interrupts on the ADXL343
    g_int_config_enabled.bits.activity = true;
    g_int_config_enabled.bits.inactivity = true;
    accel.enableInterrupts(g_int_config_enabled);

    //map the activity interrupt to INT1 and inactivity interrupt to INT2
    g_int_config_map.bits.activity = ADXL343_INT1;
    g_int_config_map.bits.inactivity = ADXL343_INT2;
    accel.mapInterrupts(g_int_config_map);
}

/**
 * Name: config_adxl
 * Inputs: void
 * Returns: void
 * Configuration for the ADXL343
*/
void config_adxl(void) {
    //check if adxl is connected
    if(!accel.begin()) {
        Serial.println("Oops, no ADXL343 detected ... Check your wiring!");
        while(1);
    }
    //set to maximum sensitivity of ADXL343
    accel.setRange(ADXL343_RANGE_2_G);

    //set activity and inactivity threshold register, scale factor is 62.5 mg/LSB
    accel.writeRegister(0x24, 20);
    accel.writeRegister(0x25, 100);
    accel.writeRegister(0x26, 4); // 4 seconds

    //turn on XYZ axis and AC mode for activity and inactivity interrupts
    accel.writeRegister(0x27, 255); //ACT_INACT_CTL register to 11111111

    //configure INT1/INT2
    config_interrupts();
}

void config_bme(void) {
    if (!bme.begin()) {
        Serial.println("Could not find a valid BME280 sensor, check wiring");
        //print sensor id for debugging
        Serial.print("SensorID was: 0x"); Serial.println(bme.sensorID(),16);
        while (1);
    }
}

/**
 * Name: config_sd
 * Inputs: void
 * Returns: void
 * Configuration for the SD module
*/
void config_sd() {
    pinMode(10, OUTPUT); //CS for SD module, CS is pin 10

    // check if sd card is connected
    if (!SD.begin(10)) {
        Serial.println("no SD card detected, check wiring");
        while(1);
    }

    //clear SD card data
    SD.remove("activity.txt");
    SD.remove("data.txt");
    SD.remove("humidity.txt");
}

/**
 * Name: setup
 * Inputs: void
 * Returns: void
 * Built-in function for Arduino, runs once at the start of the program,
 * used for initialization
*/
void setup() {
    // initialize Serial Monitor at 9600 baud
    Serial.begin(baud_rate);
    while (!Serial); //pause program and wait for serial monitor initialization

    //check if rtc is connected
    if (!rtc.begin()) {
        Serial.println("RTC not found");
        while(1);
    }

    config_sd();
    config_adxl();
    config_bme();

    //print title and skip a line
    Serial.println("WASTS V0.3");
    Serial.println("");
}

/**
 * Name: loop
 * Inputs: void
 * Returns: void
 * built-in function for Arduino, runs consecutively after setup function ends
*/
void loop() {
    //get current time from rtc
    DateTime now = rtc.now();

    //get current time to check if time to read from bme280
    //unsigned long currentMillis = millis();

    //get sensor event
    sensors_event_t event;
    accel.getEvent(&event);

    delay(print_delay); //pause to allow arduino time to process and print to serial

    //triggers when activity detected
    while (g_int1_fired) {

        /* Print to SD card
        // --------------------------------*/
        //write data with timestamp to data.txt on SD card
        File activity = SD.open("activity.txt", FILE_WRITE);

        //timestamp
        activity.print(now.hour(), DEC); activity.print(':');
        activity.print(now.minute(), DEC); activity.print(':');
        activity.print(now.second(), DEC);

        activity.println("activity detected");

        //print the acceleration data from the moment activity detected
        activity.print(event.acceleration.x); activity.print(" ");
        activity.print(event.acceleration.y); activity.print(" ");
        activity.println(event.acceleration.z);

        //print the number of times activity detected to sd card
        activity.print("\tActivity Count: "); activity.println(g_int_stats.activity, DEC);

        Serial.println("Activity Detected");

        //clear interrupt by checking the source and decrementing counter
        uint8_t source = accel.checkInterrupts();
        g_int1_fired--;
        activity.close(); //save file on SD card
    }

    //write data with timestamp to data.txt on SD card
    File data = SD.open("data.txt", FILE_WRITE);

    //triggers when inactivity detected
    while (g_int2_fired) {

        /* Print to SD card
        --------------------------------*/

        //timestamp
        data.print(now.hour(), DEC); data.print(':');
        data.print(now.minute(), DEC); data.print(':');
        data.print(now.second(), DEC);

        //print the acceleration data from the moment inactivity detected to
        data.print(event.acceleration.x); data.print(" ");
        data.print(event.acceleration.y); data.print(" ");
        data.println(event.acceleration.z);

        //print the number of times inactivity detected to sd card
        data.print("\tInactivity Count: "); data.println(g_int_stats.inactivity, DEC);

        Serial.println("inactivity detected"); //debugging

        //clear interrupt by checking the source and decrementing counter
        uint8_t source = accel.checkInterrupts();
        g_int2_fired--;
    }
    data.close(); //save file on SD card

    //check if time to read from bme280
    File humidity = SD.open("humidity.txt", FILE_WRITE);

    if (currentMillis - previousMillis >= read_interval) {
        //save last time bme280 read
        previousMillis = currentMillis;

        /* Print humidity to SD card
        --------------------------------*/

        //timestamp
        humidity.print(now.hour(), DEC); humidity.print(':');
        humidity.print(now.minute(), DEC); humidity.print(':');
        humidity.print(now.second(), DEC); humidity.print(" ");

        //humidity data
        humidity.println(bme.readHumidity());
    }
    humidity.close(); //save file on SD card
}

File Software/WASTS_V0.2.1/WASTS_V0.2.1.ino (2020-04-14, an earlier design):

/*******************************************************************************
WASTS
Rachel Bai
v0.2.1
Last edited: 8/25/19

Collects data from ADXL343 accelerometer using the activity HW interrupt and
continous polling, then prints the timestamp and data to the serial monitor and
micro-SD card.

HW Config:
Arduino Nano
micro-SD module
ADXL343

UPDATE: uses activity interrupt from ADXL343 for data collection

Libraries from Arduino and Adafruit
*******************************************************************************/

//add inactivity
#include <Wire.h>
#include <RTClib.h>
#include <SD.h>
#include <Adafruit_Sensor.h>
#include <Adafruit_ADXL343.h>

//constants
const int baud_rate = 9600;
const int print_delay = 30;

//assign an I2C address to the ADXL343
Adafruit_ADXL343 accel = Adafruit_ADXL343(12345);

RTC_DS3231 rtc; //create RTC object
File data; //create new file on SD card to store data in

//pin for activity interrupt on the Arduino
const int INPUT_PIN_INT1 = 2;

//struct stores the # of activity interrupts fired
struct adxl_int_stats {
    uint32_t activity;
};

struct adxl_int_stats g_int_stats = { 0 }; //global stats block
uint32_t g_ints_fired = 0; //counter for number of unused interrupts
int_config g_int_config_enabled = { 0 }; //variable for enabled interrupts
int_config g_int_config_map = { 0 }; //variable for mapping INT pin interrupts


/**
 * Name: int1_isr
 * Inputs: void
 * Returns: void
 * Interrupt service routine for INT1 pin event, triggers interrupt handler in
 * the main loop and increments counter for number of times the activity interrupt
 * is triggered
*/
void int1_isr(void) {
    g_int_stats.activity++; //counter
    g_ints_fired++; //trigger interrupt handler in loop
}

/**
 * Name: config_interrupts
 * Inputs: void
 * Returns: void
 * Configuration for the ADXL343 INT1 HW interrupt
*/
void config_interrupts(void) {
    //attach the INT1 input pin on the Arduino to the ISR for the INT1 on the ADXL343
    pinMode(INPUT_PIN_INT1, INPUT);
    attachInterrupt(digitalPinToInterrupt(INPUT_PIN_INT1), int1_isr, RISING);

    //enable only the activity interrupt on the ADXL343
    g_int_config_enabled.bits.activity = true;
    accel.enableInterrupts(g_int_config_enabled);

    //map the activity interrupt to INT1
    g_int_config_map.bits.activity = ADXL343_INT1;
    accel.mapInterrupts(g_int_config_map);
}

/**
 * Name: setup
 * Inputs: void
 * Returns: void
 * Built-in function for Arduino, runs once at the start of the program,
 * initialization for program
*/
void setup() {
    Serial.begin(baud_rate);

    pinMode(10, OUTPUT); //CS for SD module, CS is pin 10

    while (!Serial); //pause program and wait for serial monitor initialization

    //initialization
    if(!accel.begin()) {
        Serial.println("Oops, no ADXL343 detected ... Check your wiring!");
        while(1);
    }
    if (!SD.begin(10)) {
        Serial.println("no SD card detected, check wiring");
        while(1);
    }
    if (!rtc.begin()) {
        Serial.println("RTC not found");
        while(1);
    }

    //print title and skip a line
    Serial.println("WASTS V0.2.1");
    Serial.println("");

    //set to maximum sensitivity of ADXL343
    accel.setRange(ADXL343_RANGE_2_G);

    //set activity threshold register, scale factor is 62.5 mg/LSB
    accel.writeRegister(0x24, 20);

    //turn on XYZ axis and AC mode in ACT_INACT_CTL register to 1110000, dec = 112
    accel.writeRegister(0x27, 112);

    //configure INT1
    config_interrupts();

    //clear SD file
    SD.remove("data.txt");
}

/**
 * Name: loop
 * Inputs: void
 * Returns: void
 * built-in function for Arduino, runs consecutively after setup function ends
*/
void loop() {
    //get current time from rtc
    DateTime now = rtc.now();

    //get sensor event
    sensors_event_t event;
    accel.getEvent(&event);

    delay(print_delay); //allow arduino time to process and print to serial

    //trigger when activity detected
    while (g_ints_fired) {

        //write data with timestamp to data.txt on SD card
        File data = SD.open("data.txt", FILE_WRITE);

        //timestamp
        data.print(now.hour(), DEC); data.print(':');
        data.print(now.minute(), DEC); data.print(':');
        data.print(now.second(), DEC);

        data.println("activity detected");

        //print the acceleration data from the moment activity detected
        data.print(event.acceleration.x); data.print(" ");
        data.print(event.acceleration.y); data.print(" ");
        data.println(event.acceleration.z);

        //print timestamp to serial monitor
        Serial.print(now.hour(), DEC); Serial.print(':');
        Serial.print(now.minute(), DEC); Serial.print(':');
        Serial.println(now.second(), DEC);

        //print the acceleration data from the moment activity detected
        Serial.print(event.acceleration.x); Serial.print(" ");
        Serial.print(event.acceleration.y); Serial.print(" ");
        Serial.println(event.acceleration.z);

        //print the number of times activity detected to sd card
        data.print("\tActivity Count: "); data.println(g_int_stats.activity, DEC);
        data.close(); //save file on SD card

        //print the number of times activity detected to serial monitor
        Serial.println("Activity detected!");
        Serial.print("\tActivity Count: "); Serial.println(g_int_stats.activity, DEC);

        //clear interrupt by checking the source and decrementing counter
        uint8_t source = accel.checkInterrupts();
        g_ints_fired--;
    }
}

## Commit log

2020-01-26 Added millis time counter and improved formatting
2020-02-02 Organized files
    [Materials List.xlsx, box lid.stl, box_updated.stl, case.stl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]
2020-02-29 Updated 3D model
    [box lid v3.stl, box v3.stl]
2020-04-14 Reorganized files
    [BOM.xlsx, Final BOM.xlsx, Materials List.xlsx, WASTS box body.stl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]
